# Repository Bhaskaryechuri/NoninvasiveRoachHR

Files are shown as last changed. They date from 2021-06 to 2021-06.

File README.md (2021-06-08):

_Author: [Bhaskar Yechuri](bhaskar.yechuri@gmail.com), Engineering Technician & Research Assistant at the [Phil Matthews Lab](http://www.matthewslab.zoology.ubc.ca/index.html), University of British Columbia - Vancouver (Last Updated: June 2021)_

# Non-Invasive Cockroach Heart Rate Monitor
A device &amp; method developed to non-invasively measure cockroach heart rate of a free-roaming cockroach.

# Summary

This photoplethysmographic device, inspired by the methods of [this paper](https://aslopubs.onlinelibrary.wiley.com/doi/abs/10.4319/lom.2013.11.91) and mounted directly onto the roach's sclerites, uses infrared LEDs and two phototransistors (i.e. IR sensors) to noninvasively monitor cockroach heart rate in real-time. [Here is a video of it in action](https://drive.google.com/file/d/15U84yjhjsBKMVfOA489h0GwnW5KllRH3/view?usp=sharing).

The system consists of the following components:
* [3D-Printed Mount](https://github.com/Bhaskaryechuri/NoninvasiveRoachHR/tree/main/mechanical): A plastic structure attached to the roach's back along the midline using melted bikini wax. This structure firmly holds the mini-PCB's LEDs & sensors close to the roach's sclerites.
* [mini-PCB](https://github.com/Bhaskaryechuri/NoninvasiveRoachHR/tree/main/circuit): Placed on the roach via the 3D-printed mount. Contains the LEDs and sensors that allow for heart rate sensing, and a symmetrical 5-pin header which can be used to conduct sensor signals out of the board and power in (GND-Signal1-5V-Signal2-GND)
* Auxiliary Board: A simple circuit connecting to the mini-PCB via a 5-pin ribbon cable, routing the outgoing signals to two independent BNC outputs and connecting the 5V power supply terminals to the mini-PCB

# Fabrication & Assembly

This section contains information on how to assemble the device from scratch.

_NOTE: If you are working with an already-fabricated device, you can skip this step._  

**Mini-PCB**:

1. From the `circuit` folder in this repository, download the ".SCH" and ".BRD files" and open them in [AutoCAD EAGLE](https://www.autodesk.ca/en/products/eagle/free-download)
2. Navigate to the board-view and click "ratsnest", which will create the ground plane
3. The simplest way to create the PCB would be to order it from a third-party PCB manufacturer (e.g. PCBWay, JLPCB, etc.), which are cheap, have a relatively short turnaround time, and minimize human error when compared to milling it using the CNC. To do this, each manufacturer requires a set of auto-generated outputs from EAGLE. If you get the PCBs manufactured externally, skip to Step 6
4. Export the .GBR and .XLN files and use those along with [FlatCAM](http://flatcam.org/) (only works on Windows) to generate CNC gcode files
5. Use the gcode files to mill out PCBs using the Carbide CNC machine
    1. It is recommended to try a few test runs on the CNC machine with used/scrap PCBs
6. Once the PCBs are ready, solder on the components according to the schematic & layout seen in the EAGLE files
7. Use heatshrink tubing to neatly seal the area around the LEDs to prevent light leaking out from the sides and into the adjacent sensors. Snip off the top of the tubing to ensure that only the sides of the LEDs are obscured, not the tops

**3D-printed mount**:

1. From the `mechanical` folder in this repository, download the ".STL" file and open it in [Ultimaker Cura](https://ultimaker.com/software/ultimaker-cura)
2. Align the flat surface of the mount to the build plate in Ultimaker Cura, choose the appropriate printer type, and set the infill to 100% with the ABS material
3. Click the "Slice" button and look at the "Preview" tab to ensure that the smaller features of the mount will be printed. If not, modify the print settings
4. Finally, save the gcode produced by the Ultimaker Cura to a flash drive and plug the drive into the lab 3D printer. Ensure that the material installed is ABS and print the file

**Auxiliary Board**:

1. Solder another 5-pin female header into a proto-board and connect additional jumpers to route the outer pins to their appropriate connections    
    1. (1 and 5) to GND, 
    2. the center pin (3) to 5V, and 
    3. the middle pins (2 and 4) to independent BNC outputs (i.e. signal1 and signal2)
1. During experiments, connect the BNC cables to this auxiliary board and the power supply terminals to the appropriate locations on the board. Do not leave the power supply connected when not in use.

# Usage Instructions

Once you have an assembled device ready to use, follow these steps to successfully read a heart rate signal from a cockroach:
1. First, test the electrical parts by connecting the mini-PCB and auxiliary board with the 5-pin ribbon cable. Connect the BNC outputs to a data logging program (e.g. LabChart + PowerLab), and connect the 5V power supply to the auxiliary board
    1. To test whether the sensors and LEDs are working as expected, place a sheet of paper in front of the LEDs and sensors to see whether the sensor voltage decreases on your computer screen. This shows that the LEDs are shining light outward, which then is reflecting back onto the sensors, resulting in the sensor voltage reacting accordingly. Make sure to unplug the power supply when you are done testing!
1. Attach the mini-PCB onto the mount in a secure but reversible way. A small amount of transparent, residue-free tape works well
2. Next, narcotize the cockroach using CO2 for ~30s. This will immobilize it for a few minutes to allow for easy mounting of the mount and board
3. Microwave bikini wax until it has the consistency of honey (but ensure it is not hot enough to burn your skin or the cockroach) and use it to attach the 3D printed mount onto the third sclerite of the cockroach. Use the "wings" of the mount as the wax attachment surfaces, to ensure that the sensors and LEDs are not obscured by wax and to make them fit flush with the surface of the sclerite. Ensure that the sensors and LEDs are aligned with the midline of the roach, on the roach's 3rd sclerite
4. Once the mount and mini-PCB are attached firmly to the roach, connect the mini-PCB to the auxiliary board using the 5-pin ribbon cable. Finally, connect the auxiliary board to the power supply. As the cockroach slowly wakes up from being narcotized, the two signals should slowly become visible on your computer screen. It helps to manually rescale the axes on the screen to zoom into the heart rate signals being produced. Signals will typically range from 2-20mV in amplitude (peak-to-peak), depending on how closely your sensors and LEDs are to the surface of the roach

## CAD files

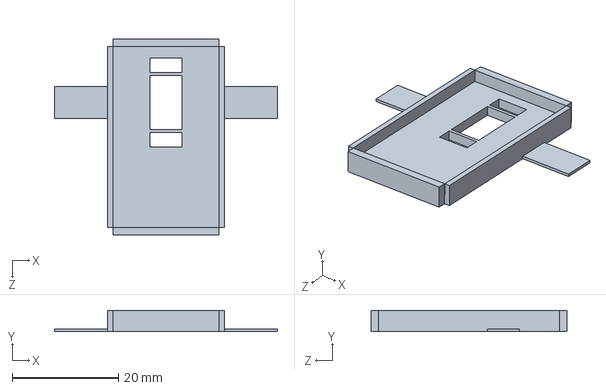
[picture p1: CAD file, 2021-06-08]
mechanical/Board-Fitted Mount with wings.SLDPRT
42.0 x 4.00 x 37.0 mm

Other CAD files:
mechanical/Board-Fitted Mount with wings.STL

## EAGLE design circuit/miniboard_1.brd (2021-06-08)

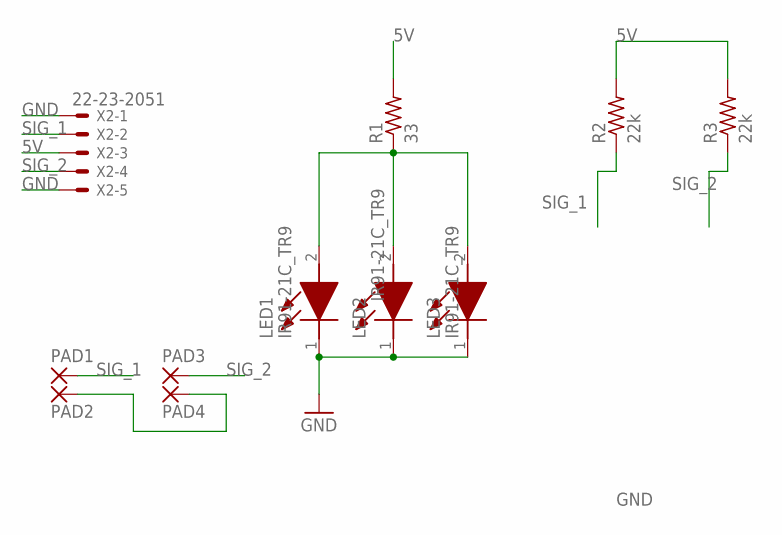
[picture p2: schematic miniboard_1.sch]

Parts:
LED1, LED2, LED3: IR91-21C_TR9; SODFL7422X280N
PAD1, PAD2, PAD3, PAD4: SMD2; SMD1,27-2,54
R1: 33; 0204/5
R2, R3: 22k; 0204/5
X2: 22-23-2051

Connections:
5V: R1.2, R2.2, R3.2, X2.3
GND: LED1.1 (K), LED2.1 (K), LED3.1 (K), PAD2.1, PAD4.1, X2.1, X2.5
unnamed: LED1.2 (A), LED2.2 (A), LED3.2 (A), R1.1
SIG_1: PAD1.1, R2.1, X2.2
SIG_2: PAD3.1, R3.1, X2.4

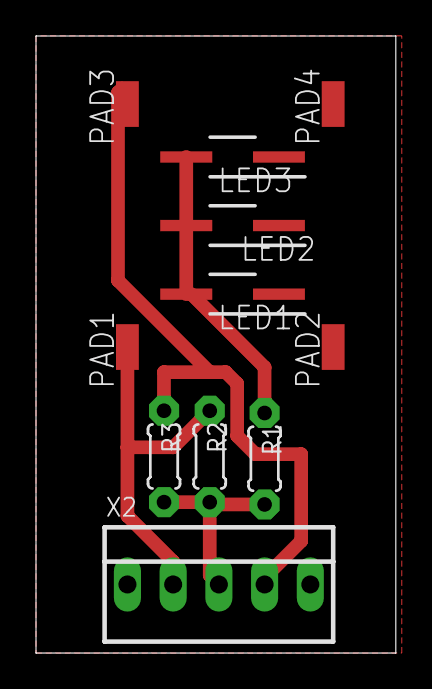
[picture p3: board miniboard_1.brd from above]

Board: 2 copper layers, 20.0 x 34.3 mm, 11 parts (0 on the bottom side), 5 nets.

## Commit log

2021-06-08 Add files via upload
    Solidworks file (editable) + STL file (printable through Ultimaker Cura) for the Cockroach-Mounted piece
    [Board-Fitted Mount with wings.SLDPRT, Board-Fitted Mount with wings.STL]
2021-06-08 Add files via upload
    uploading pcb design files
    [miniboard_1.brd, miniboard_1.sch]
